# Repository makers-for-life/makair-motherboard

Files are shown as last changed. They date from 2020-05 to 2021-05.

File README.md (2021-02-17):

# MakAir Motherboard

## Versions

| Version | Last Changelog | Ready? | Schematics | Live CAD Models |
| ------- | -------------- | ------ | ---------- | --------------- |
| V1.1 | Working PCB w/ software | ✅ | none | none
| V2.0 | Version Two | ✅ | [view schematic](./src/schematics/Archives/V2/Electrical%20Schematics.pdf) | none
| V3.0 | Added pressure sensors + more systems have been integrated on the board | ✅ | [view schematic](./src/schematics/V3/Electrical%20Schematics.pdf) | [view model](https://a360.co/3eaMoN0)

## Notes

* All the electronics schematics and PCB designs were made by engineers from [Tronico](https://www.tronico-alcen.com/en), a France-based electronic systems designers and manufacturer, with on-site PCB manufacturing capabilities.

## Renders

### Final Motherboard

<p align="center">
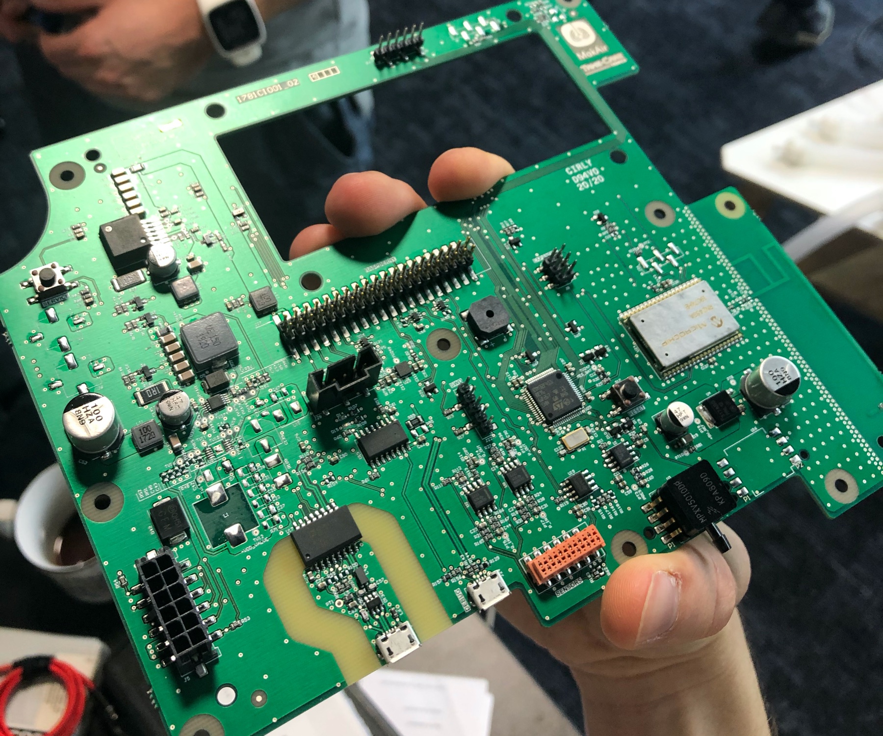
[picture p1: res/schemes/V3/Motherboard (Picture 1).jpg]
Motherboard Picture
  
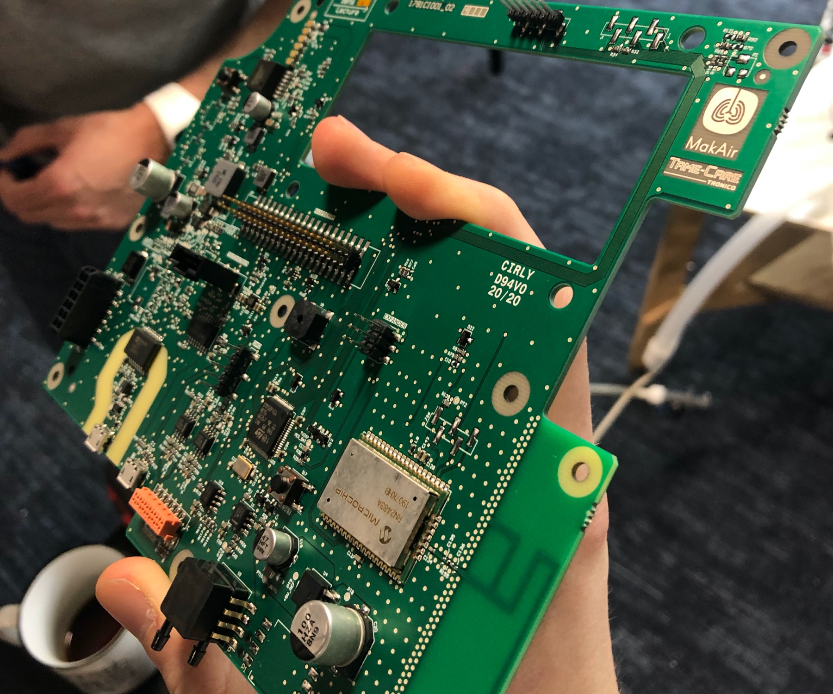
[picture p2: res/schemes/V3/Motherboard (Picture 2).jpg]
Motherboard Picture
  
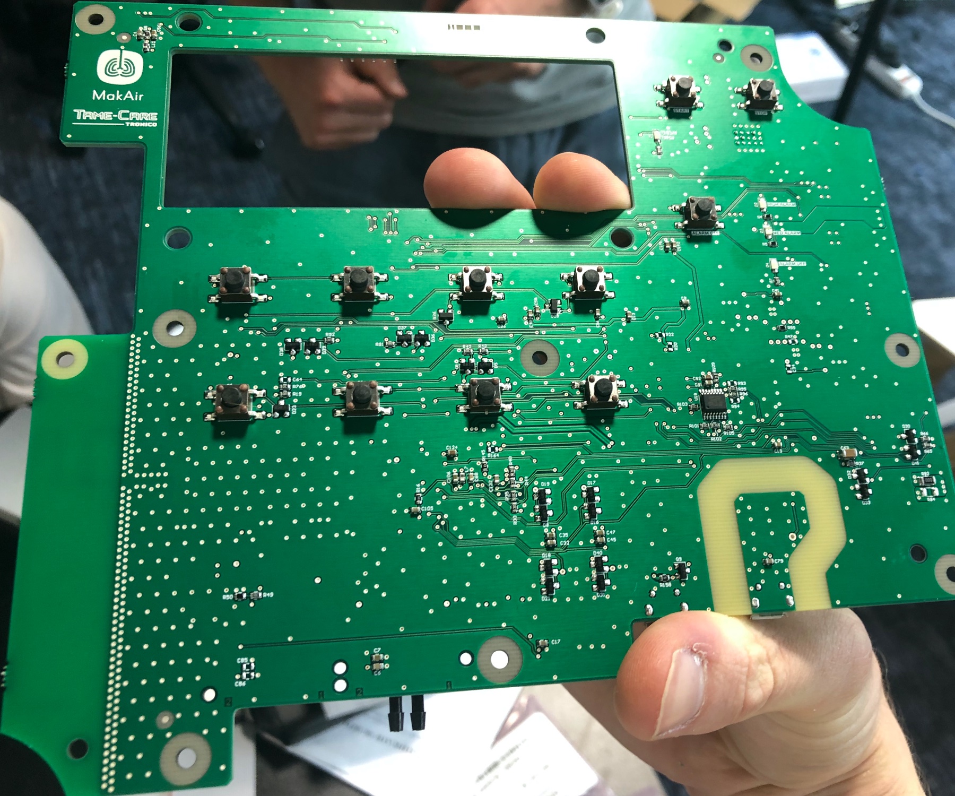
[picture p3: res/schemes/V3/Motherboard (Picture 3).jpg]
Motherboard Picture
  
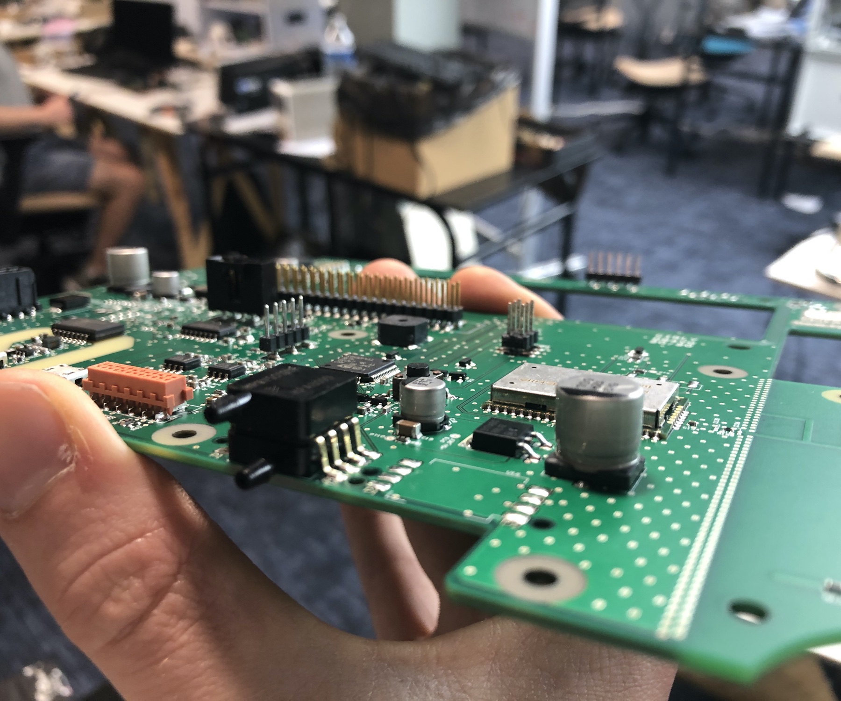
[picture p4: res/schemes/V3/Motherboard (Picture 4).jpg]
Motherboard Picture
  
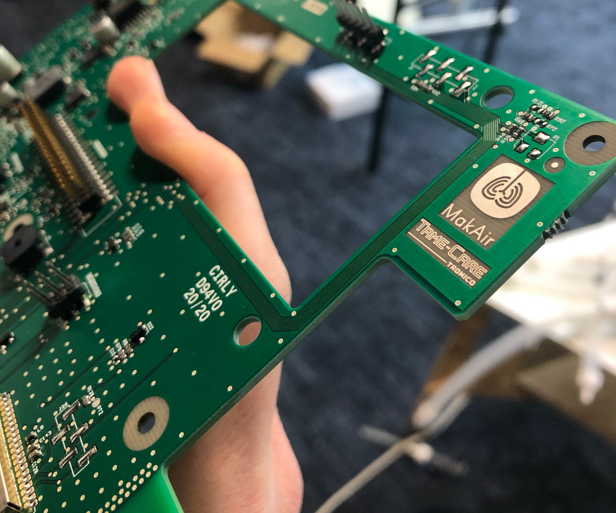
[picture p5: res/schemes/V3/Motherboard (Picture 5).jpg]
Motherboard Picture
  
</p>

### Gerbers

<p align="center">
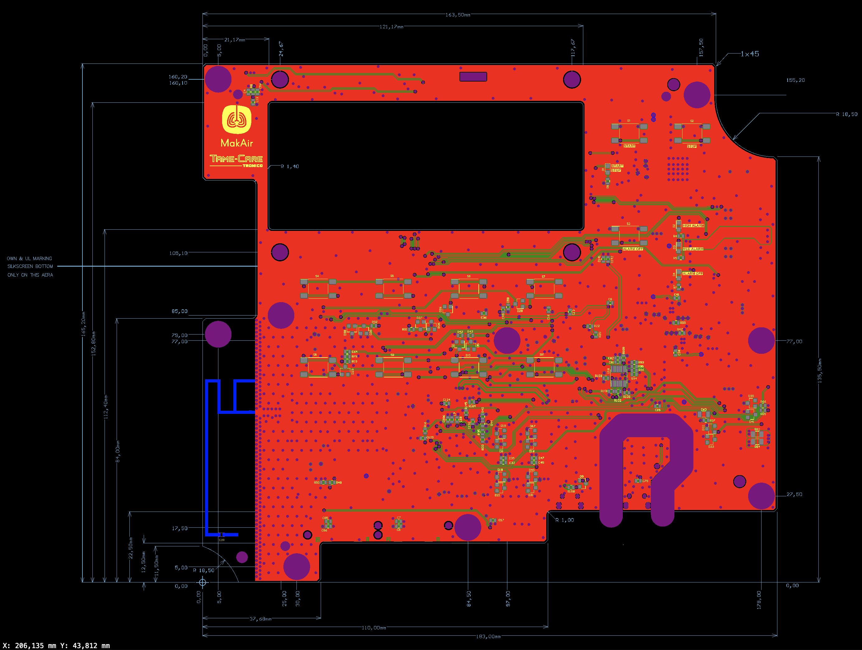
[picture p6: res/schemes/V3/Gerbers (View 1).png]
Gerbers View
  
</p>

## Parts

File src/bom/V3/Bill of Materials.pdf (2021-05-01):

Designation : RESP. ARTIFICIEL V3.1 | | Author by : vlecunff
Customer : TRONICO | Date : 28/05/2020 | Signature :
Reference : 1781LC001 | Revision : 02 | Verified by : pboiziau
Customer Reference : 099 | | Signature :
Level | Reference designator | ID_RnD | Item Code | Description | Quantity | Commentary
1 | 2 | 3 | 4 | | | | Short Description | Long Description | Manufacturer & Part Number
* | | | | C1-C6,C8,C11-C17,C23,C24,C30-C32,C36,C41,C44,C45,C49,C 58,C60-C62,C66,C69,C71,C72,C74,C 76-C81,C88-C90,C92-C97,C105,C107,C127,C128,C 131,C132,C142 | 23U00036 | 00280K676A | COND_CERAM CMS 0603 X7R | 100nF 50V 10% -55°C/+125°C | AVX 06035C104KAT2A | 55
* | | | | C7,C35,C47,C56,C59,C70,C8 3,C91,C106,C111-C113,C141,C143 | 23U00347 | 00280K522A | COND_CERAM CMS 0603 X5R | 1uF 50V 10% -55°C/+85°C | TDK CGA3E3X5R1H105K080AB | 14
* | | | | C9 | 23U00388 | 00280K526A | COND_CERAM CMS 0603 C0G | 470pF 50V 5% -55°C/+125°C | KEMET C0603C471J5GACTU | 1
* | | | | C10,C34,C64,C65,C73,C85,C 130 | | | | | | NC
* | | | | C18,C98,C140 | 21U00041 | 002504131A | COND_ALUM CMS D:6.3mm | 47uF 50V 20% 680mR -55°C/+105°C | PANASONIC EEEFT1H470AP | 3
* | | | | C19,C25,C26,C37-C40,C63,C99 | 23U00488 | 00280K521A | COND_CERAM CMS 1206 X5R | 10uF 50V 10% -55°C/+85°C | MURATA GRM31CR61H106KA12L | 9
* | | | | C20,C53 | 21U00015 | 002504142A | COND_ALUM CMS D:10mm | 100uF +50V 20% 28mR -55°C/+105°C | PANASONIC EEHZA1H101P | 2
* | | | | C21,C22,C27-C29,C33,C67 | | | | | | NC
* | | | | C42 | | | | | | NC
* | | | | C43 | | | | | | NC
* | | | | C46 | | | | | | NC
* | | | | C48,C54 | | | | | | NC
* | | | | C50 | 23U00055 | 00280K524A | COND_CERAM CMS 0603 C0G | 6.8pF 50V 0.25pF -55°C/+125°C | KEMET C0603C689C5GACTU | 1
* | | | | C51 | 23U00490 | 00280K523A | COND_CERAM CMS 0603 X7R | 4.7nF 50V 5% -55°C/+125°C | KEMET C0603C472J5RACTU | 1
* | | | | C52,C68 | 23U00104 | 00280K634A | COND_CERAM CMS 0603 X7R | 10nF 50V 10% -55°C/+125°C | KEMET C0603C103K5RACTU | 2
* | | | | C55,C57,C122,C123 | 23U00046 | 00280K636A | COND_CERAM CMS 0603 C0G | 22pF 50V 10% -55°C/+125°C | KEMET C0603C220K5GACTU | 4
* | | | | C82,C124 | 23U00282 | 00280K682A | COND_CERAM CMS 0603 X5R | 4.7uF 25V 10% -55°C/+85°C | MURATA GRM188R61E475KE15D | 2
* | | | | C86 | | | | | | NC
* | | | | C100-C104,C114 | 23U00492 | 00280K635A | COND_CERAM CMS 1206 X5R | 22µF 25V 20% -55°C/+85°C | MURATA GRT31CR61E226ME01L | 6
* | | | | C109,C110 | 23U00059 | 00280K681A | COND_CERAM CMS 0603 X7R | 22nF 16V 10% -55°C/+125°C | KEMET C0603C223K4RACTU | 2
* | | | | C134 | 23U00494 | 00280K642A | COND_CERAM CMS 0402 COG HF | 56pF 100V 1% -55°C/+125°C | KEMET CBR04C560F1GAC | 1
* | | | | C135,C136 | | | | | | NC
* | | | | C139 | | | | | | NC
Soudure : | SAC

26 RUE DU BOCAGE CS 20660
ST PHILBERT DE BOUAINE
85607 MONTAIGU CEDEX
Tél : +33 (0)2 51 41 91 35 Fax : +33 (0)2 51 41 94 27
ET68/D | STRICTEMENT CONFIDENTIEL TRONICO | 1/5

Reference : 1781LC001 | Revision : 02 | Verified by : pboiziau
Customer Reference : 099 | | Signature :
Level | Reference designator | ID_RnD | Item Code | Description | Quantity | Commentary
1 | 2 | 3 | 4 | | | | Short Description | Long Description | Manufacturer & Part Number
* | | | | CI1 | I1U00004 | 00590G851A | CIRCUIT IMPRIME RESP. ARTIFICIEL V3.1 | 1781CI001 | SPECIF 1781PCB0001_05 PLAN 1781CI001 IND05 GERBERS 1781GER001 IND05 PANNEAU PAN099MAKR694 IND00 | 1
* | | | | D1,D4 | E1U00030 | 004109304A | DIODE_LED VERTE CMS 0805 | 520 78mW 3.4V 20mA -40°C/+85°C -40°C/+85°C | AVAGO HSMQ-C170 | 2
* | | | | D2 | E1U00031 | 004109305A | DIODE_LED ROUGE CMS 0805 | 637 60mW 2.4V 25mA -40°C/+85°C -40°C/+85°C | AVAGO HSMC-C170 | 1
* | | | | D3 | E1U00032 | 004109306A | DIODE_LED JAUNE CMS 0805 | 591 85mcd 2.05V 20mA -40°C/+85°C -40°C/+90°C | Everlight Electronics EAST2012YA2 | 1
* | | | | D5,D6,D8,D10-D12,D16-D19,D21,D30-D33,D36-D41 | 33U00013 | 00415E364A | DIODE_DE_SIGNAL CMS SOT23 | 30V 200mA -55°C/+150°C -55°C/+150°C | FAIRCHILD BAT54 | 21
* | | | | D7 | | | | | | NC
* | | | | D9 | 39U00073 | 004109287A-RD | DIODE_SCHOTTKY CMS SMB | 40V 3A SINGLE -40°C/+105°C -65°C/+150°C | ST MICROELECTRONICS STPS340U | 1
* | | | | D13 | 38U00032 | 00415E388A | DIODE_ESD CMS SOT23-6L UNI | 15kV DUAL -40°C/+125°C -55°C/+150°C | ST MICROELECTRONICS USBLC6-2SC6 | 1
* | | | | D14,D15,D20 | E1U00022 | 00415E387A | DIODE_LED VERTE CMS 0402 | 574nm 3.5mcd 1.9V 2mA -40°C/+85°C -40°C/+85°C | KINGBRIGHT APHHS1005LCGCK | 3
* | | | | D22-D29 | 33U00002 | 00415E389A | DIODE_DE_SIGNAL CMS SOT23 | 85V 200mA -55°C/+150°C -55°C/+150°C | FAIRCHILD BAS16 | 8
* | | | | D34 | 38U00011 | 00415E415A | DIODE_ESD CMS SOT553 UNI | 8kV 0.9V-5.5V DUAL -40°C/+85°C -65°C/+150°C | TEXAS INSTRUMENTS TPD2E001DRLR | 1
* | | | | D42 | 36U00007 | 00415E363A | DIODE_TRANSIL CMS DO-214AB BI | 33V 1500W -55°C/+150°C -55°C/+150°C | FAIRCHILD SMCJ33CA | 1
* | | | | ET1 | G1U00004 | - | ETIQUETTE IDENTIFICATION | 1781ET001 | PLAN 1781ET001 IND01 | 1
| * | | | - | - | CONSOM1071 | ETIQU ETIQU POLYIMIDE AMBRE MAT | | BRADY THT-46-724-10 | 1
* | | | | F1 | 86U00021 | 00555A448A | FUSIBLE REARMABLE CMS 0603 | 500mA 6V THERM -40°C/+85°C | BOURNS MF-FSMF050X | 1
* | | | | J1,J3 | ABU00030 | 005169144A | BARRETTE MALE CMS 6PTS | DROIT SN P:2.54mm -55°C/+105°C | SAMTEC TSM-106-01-T-SV-P-TR | 2
* | | | | J2,J24 | A7U00249 | 005169160A | CONNECT USB CMS 5PTS | EMBASE RECT FEM COUDE -30°C/+85°C | HIROSE ZX62D-B-5PA8(30) | 2
* | | | | J4 | A7U00321 | 005169147A | CONNECT Micro Match CMS 12PTS | EMBASE RECT FEM DROIT | TE CONNECTIVITY 1-188275-2 | 1
* | | | | J5 | A7U00305 | 005169145A | CONNECT MICRO-FIT CMS 2x6PTS | EMBASE RECT MALE DROIT -40°C/+105°C -40°C/+105°C | MOLEX 43045-1218 | 1
Soudure : | SAC

26 RUE DU BOCAGE CS 20660
ST PHILBERT DE BOUAINE
85607 MONTAIGU CEDEX
Tél : +33 (0)2 51 41 91 35 Fax : +33 (0)2 51 41 94 27

Reference : 1781LC001 | Revision : 02 | Verified by : pboiziau
Customer Reference : 099 | | Signature :
Level | Reference designator | ID_RnD | Item Code | Description | Quantity | Commentary
1 | 2 | 3 | 4 | | | | Short Description | Long Description | Manufacturer & Part Number
* | | | | J6,J7 | | | | | | NC
* | | | | J8 | A7U00323 | 005169124A | CONNECT C-Grid CMS 2x3PTS | EMBASE RECT MALE DROIT -40°C/+105°C | MOLEX 0015912060 | 1
* | | | | J9 | A7U00339 | 005169170A | CONNECT PCB HEADER CMS 4PTS | EMBASE RECT MALE DROIT -25°C/+85°C | JST B4B-PH-SM4-TB(LF)(SN) | 1
* | | | | J10 | | | | | | NC
* | | | | J22 | A7U00320 | 005169159A | BARRETTE MALE CMS 5PTS | DROIT SN P:2.54mm -55°C/+105°C | SAMTEC TSM-105-01-T-SV | 1
* | | | | J26 | | | | | | NC
* | | | | J27 | A7U00330 | 005169149A | CONNECT CMS 2x20PTS | EMBASE RECT MALE DROIT -40°C/+105°C | CNC TECH 3020-40-0300-00 | 1
* | | | | J28 | A7U00327 | 005169148A | CONNECT SL CMS 5PTS | EMBASE RECT MALE DROIT -40°C/+105°C | MOLEX 74099-1005 | 1
* | | | | L1 | | | | | | NC
* | | | | L3 | 42U00158 | 003115800A | SELF CMS 1040 | 15uH 20% 8.5A -40°C/+125°C | WURTH ELEKTRONIK 74437368150 | 1
* | | | | L4 | 48U00023 | 003115846A | SELF_MODE_COMMUN CMS 1206TS | 90R 25% 370mA 50V -40°C/+125°C | PULSE ELECTRONICS PE-1206CCMC900STS | 1
* | | | | L5,L6 | 43U00020 | 003115845A | FERRITES CMS 0603 | 600R 100MHz 200mA -55°C/+125°C -20°C/+60°C | WURTH ELEKTRONIK 74279265 | 2
* | | | | L7 | 42U00090 | 003115847A | SELF CMS 0603 | 120nH 5% 300mA -40°C/+85°C | KEMET L0603CR12JRMST | 1
* | | | | L8,L12 | 43U00016 | 003115836A | FERRITES CMS 0603 | 220R 100MHz 2.5A -55°C/+125°C -55°C/+125°C | MURATA BLM18SG221TN1D | 2
* | | | | L10 | | | | | | NC
* | | | | L11,L13,L16 | 42U00140 | 003115837A | SELF CMS 5.2x5.7x1.8mm | 10µH 20% 3.4A -40°C/+150°C -40°C/+150°C | BOURNS SRP5020TA-100M | 3
* | | | | P1 | | | | | | NC
* | | | | Q1,Q2,Q4-Q8 | 92U00012 | 004234241A | TRANSISTOR_MOS CMS SOT23 | CANAL N 60V 0.36A -55°C/+150°C -65°C/+150°C | NEXPERIA 2N7002P,215 | 7
* | | | | Q3 | 92U00048 | 004234251A | TRANSISTOR_MOS CMS SOT23-6L | CANAL P 30V 4A -55°C/+150°C | ST MICROELECTRONICS STT4P3LLH6 | 1
* | | | | Q9 | 91U00003 | 004234238A | TRANSISTOR_BIP CMS SOT23 | NPN 30V +0.6A -55°C/+150°C -55°C/+150°C | ON SEMICONDUCTOR MMBT2222LT1G | 1
* | | | | R1,R7,R9,R10,R19,R32,R43,R 53,R54,R63,R72-R74,R83,R91,R92,R131,R136 ,R147-R150,R168,R170 | 11U00071 | 00140AA4045A | REST CMS 0603 100PPM | 100R 1/10W 1% -55°C/+155°C | YAGEO RC0603FR-07100RL | 24
* | | | | R2,R3,R6,R11,R27,R31,R33-R35,R41,R42,R57,R59-R61,R64,R75-R77,R87,R88,R95-R98,R101-R103,R105,R111,R116,R117, R119,R130,R135,R139,R151-R154,R156,R165 | 11U00108 | 00140AA4035A | REST CMS 0603 100PPM | 10kR 1/10W 1% -55°C/+155°C | YAGEO RC0603FR-0710KL | 42
Soudure : | SAC

26 RUE DU BOCAGE CS 20660
ST PHILBERT DE BOUAINE
85607 MONTAIGU CEDEX
Tél : +33 (0)2 51 41 91 35 Fax : +33 (0)2 51 41 94 27

Reference : 1781LC001 | Revision : 02 | Verified by : pboiziau
Customer Reference : 099 | | Signature :
Level | Reference designator | ID_RnD | Item Code | Description | Quantity | Commentary
1 | 2 | 3 | 4 | | | | Short Description | Long Description | Manufacturer & Part Number
* | | | | R4,R5 | 11U01011 | 00140AA4043A | REST CMS 0603 200PPM | 180R 1/10W 1% 75V -55°C/+155°C | VISHAY CRCW0603180RJNEA | 2
* | | | | R8,R26 | 11U00074 | 00140AA4042A | REST CMS 0603 100PPM | 150R 1/10W 1% -55°C/+155°C | YAGEO RC0603FR-07150RL | 2
* | | | | R12,R69,R79,R81,R90,R109, R123-R128,R143-R145,R163 | 11U00009 | 00140AA4037A | REST CMS 0603 100PPM | 0R 1/10W 20mR -55°C/+155°C | VISHAY CRCW06030000Z0EA | 16
* | | | | R13,R17,R106,R110 | 11U01018 | 00140AA4054A | REST CMS 0603 100PPM | 33R 1/10W 5% 75V -55°C/+155°C | YAGEO RC0603JR-0733RL | 4
* | | | | R14,R62,R70,R121,R122,R13 3,R169,R171 | | | | | | NC
* | | | | R15,R18,R21,R25,R112 | 11U00106 | 00140AA4032A | REST CMS 0603 100PPM | 220R 1/10W 1% -55°C/+155°C | YAGEO RC0603FR-07220RL | 5
* | | | | R16,R45,R158 | 11U01012 | 00140AA4047A | REST CMS 0603 100PPM | 1.6kR 1/10W 1% 75V -55°C/+155°C | VISHAY CRCW06031K60FKEA | 3
* | | | | R20,R22,R51,R93,R94,R99,R 100,R104,R115,R118,R132,R 164 | | | | | | NC
* | | | | R23,R24,R113,R166 | 11U00156 | 00140AA4039A | REST CMS 0603 100PPM | 470R 1/10W 1% -55°C/+155°C | YAGEO RC0603FR-07470RL | 4
* | | | | R28,R107,R108,R120 | 11U00072 | 00140AA4048A | REST CMS 0603 100PPM | 680R 1/10W 1% -55°C/+155°C | YAGEO RC0603FR-07680RL | 4
* | | | | R29 | 11U00585 | 00140AA4049A | REST CMS 0603 100PPM | 8.2kR 1/10W 1% -55°C/+155°C | YAGEO RC0603FR-078K2L | 1
* | | | | R30 | 11U00110 | 00140AA4038A | REST CMS 0603 100PPM | 1kR 1/10W 1% -55°C/+155°C | YAGEO RC0603FR-071KL | 1
* | | | | R36,R38,R114,R167 | 11U00282 | 00140AA4053A | REST CMS 0603 100PPM | 910R 1/10W 1% -55°C/+155°C | YAGEO RC0603FR-07910RL | 4
* | | | | R37 | 11U00977 | 00140AA4040A | REST CMS 0603 100PPM | 3kR 1/10W 1% -55°C/+155°C | YAGEO RC0603FR-073KL | 1
* | | | | R39,R161 | 11U01009 | 00140AA4034A | REST CMS 2512 100PPM | 1R 1.5W 1% 500V -55°C/+155°C | VISHAY CRCW25121R00FKEGHP | 2
* | | | | R40,R44,R134 | 11U00069 | 00140AA4125A | REST CMS 0603 100PPM | 4.7kR 1/10W 1% -55°C/+155°C | YAGEO RC0603FR-074K7L | 3
* | | | | R46 | 11U00079 | 00140AA4055A | REST CMS 0603 100PPM | 330R 1/10W 1% -55°C/+155°C | YAGEO RC0603FR-07330RL | 1
* | | | | R47 | | | | | | NC
* | | | | R48 | | | | | | NC
* | | | | R49 | 11U01020 | 00140AA3976A | REST CMS 0603 25PPM | 330R 1/10W 0.1% 75V -55°C/+85°C | PANASONIC ERA-3AEB331V | 1
* | | | | R50 | 11U00834 | 00140AA4154A | REST CMS 0603 10PPM | 1kR 1/8W 0.1% 75V -55°C/+155°C | VISHAY TNPW06031K00BYEN | 1
* | | | | R52 | | | | | | NC
* | | | | R55,R129 | 11U01019 | 00140AA4051A | REST CMS 0603 100PPM | 220kR 1/10W 1% 75V -55°C/+155°C | YAGEO RC0603FR-07220KL | 2
* | | | | R56,R157 | 11U01013 | 00140AA4046A | REST CMS 0603 100PPM | 44.2kR 1/10W 1% 75V -55°C/+155°C | VISHAY CRCW060344K2FKEA | 2
* | | | | R58 | 11U01017 | 00140AA4052A | REST CMS 0603 100PPM | 52.3kR 1/10W 1% 75V -55°C/+155°C | YAGEO RC0603FR-0752K3L | 1
* | | | | R65 | 11U01021 | 00140AA3973A | REST CMS 0603 100PPM | 200kR 1/10W 1% 75V -55°C/+155°C | YAGEO RC0603FR-07200KL | 1
* | | | | R66 | 11U00176 | 00140AA4060A | REST CMS 0603 100PPM | 27kR 1/10W 1% -55°C/+155°C | YAGEO RC0603FR-0727KL | 1
* | | | | R67 | 11U00111 | 00140AA3974A | REST CMS 0603 100PPM | 100kR 1/10W 1% -55°C/+155°C | YAGEO RC0603FR-07100KL | 1
* | | | | R68 | 11U01027 | 00140AA4124A | REST 0603 100PPM | 54.9kR 1/10W 1% 75V -55°C/+155°C | YAGEO RC0603FR-0754K9L | 1
* | | | | R71,R82,R85 | | | | | | NC
* | | | | R78,R80,R84,R89 | 11U00878 | 00140AA4050A | REST CMS 1206 | 0R 1/4W 20mR 3.5A -55°C/+155°C | VISHAY RCA12060000ZSEA | 4
* | | | | R86 | 11U01010 | 00140AA4041A | REST CMS 0603 100PPM | 62kR 1/10W 1% 75V -55°C/+155°C | VISHAY CRCW060362K0FKEA | 1
* | | | | R155 | 11U00352 | 00140AA3975A | REST CMS 0402 | 0R 20mR 1.5A -55°C/+155°C | VISHAY CRCW04020000Z0ED | 1
* | | | | R160 | | | | | | NC
* | | | | S1-S12,S17 | 81U00012 | 00580L320A | BOUTON_POUSSOIR CMS 4PTS | DROIT 12Vc.a. 50mA -35°C/+85°C | TE CONNECTIVITY 4-1437565-1 | 13
* | | | | SW1 | 82U00010 | 00580L449A | INTERRUPTEUR GLISSIERE CMS | DPDT DROIT +6Vdc;0.3A -40°C/+85°C -40°C/+85°C | C&K JS202011JCQN | 1
Soudure : | SAC

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

Reference : 1781LC001 | Revision : 02 | Verified by : pboiziau
Customer Reference : 099 | | Signature :
Level | Reference designator | ID_RnD | Item Code | Description | Quantity | Commentary
1 | 2 | 3 | 4 | | | | Short Description | Long Description | Manufacturer & Part Number
* | | | | U1,U2,U6 | 61U00068 | 00480P210A | CI_AOP_COMPAR CMS SO8 | DUAL AOP +2.2V/+5.5V L NOISE -40°C/+150°C -65°C/+150°C | TEXAS INSTRUMENTS OPA2365AIDG4 | 3
* | | | | U3 | 68U00002 | 00555A441A | CI_CAPTEUR_PRESSION CMS 1351 | ANALOG +4.75V/+5.25V 0PSI/1.45PSI 5% -40°C/+125°C -40°C/+125°C | NXP MPXV5010DP | 1
* | | | | U4 | 62U00134 | 00480P166A | CI_REGUL CMS DPAK | LIN +3V/+40V +1.2V/+37V LDO -40°C/+125°C -65°C/+150°C | ON SEMICONDUCTOR LM317MABDTRKG | 1
* | | | | U5 | | | | | | NC
* | | | | U7 | 62U00131 | 00480P000A | CI_REGUL CMS VSSOP10 | DEC +3.5V/+60V; +8V/+65V -40°C/+125°C | TEXAS INSTRUMENTS TPS54260DGQ | 1
* | | | | U8 | 74U00004 | 004412472A | BUZZER CMS 8.5x8.5x4 | TRANSD 4kHz +1V/+6V 100dBA -20°C/+70°C -40°C/+85°C | CUI INC CMT-8540S-SMT-TR | 1
* | | | | U9,U25,U26 | 67U00126 | 00480P167A | CI_DRIVER CMS SC70 | BUFFER -0.5V/+4.2V -40°C/+125°C -65°C/+150°C | TEXAS INSTRUMENTS 2N7001TDCKR | 3
* | | | | U13 | 51U00068 | 003500326A | ALIM DC/DC CMS 18W | +6V/+42V +0.8V/+6V +3A 90% -40°C/+125°C -65°C/+150°C | TEXAS INSTRUMENTS LMZ14203TZ-ADJ/NOPB | 1
* | | | | U15 | 64U00036 | 00480P020A | CI_MEMOIRE CMS SO16 | Voltage level Shifter +3V/+18V -55°C/+125°C -65°C/+150°C | TEXAS INSTRUMENTS CD40109BNSR | 1
* | | | | U16 | | | | | | NC
* | | | | U17 | 67U00125 | 00480P209A | CI_DRIVER CMS SO16W | USB +3.1V/+5.5V Isolation 5kV 12Mbps -40°C/+105°C -65°C/+150°C | ANALOG DEVICES ADUM4160BRIZ | 1
* | | | | U18 | 67U00086 | 00480P211A | CI_DRIVER CMS SSOP16 | UART/USB +2.97V/+5.5V -40°C/+85°C -65°C/+150°C | FTDI FT230XS | 1
* | | | | U19 | 64U00034 | 00480P212A | CI_MEMOIRE CMS SO8 | EEPROM +1.7V/+5.5V 2kB I2C -40°C/+85°C -65°C/+150°C | ST MICROELECTRONICS M24C02-FMN6TP | 1
* | | | | U20 | 65U00043 | 00480P113A-RD | CI_PROC CMS LQFP64 | uC +1.7V/+2.1V 8Bits 256kB -40°C/+85°C -60°C/+150°C | ST MICROELECTRONICS STM32F411RET6 | 1
* | | | | U23 | 62U00132 | 00480P165A | CI_REGUL CMS DFN6 | LIN +1.25V/+6V +3.3V/2A LDO -40°C/+125°C -55°C/+150°C | ST MICROELECTRONICS LD39200PU33R | 1
* | | | | U24 | 6FU00005 | 00480P164A | CI_MODULE CMS RN2483 LoRa | UART +2.1V/+3.6V Tx:14dBm/Rx:-148dBm 0 -40°C/+85°C -40°C/+115°C | MICROCHIP RN2483 | 1
* | | | | X1 | 73U00029 | 004412484A | QUARTZ CMS 6.0x3.6MM | 8MHZ 20PPM 18pF -20°C/+70°C -40°C/+85°C | ABRACON ABMM2-8.000MHZ-E2-T | 1
Soudure : | SAC

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

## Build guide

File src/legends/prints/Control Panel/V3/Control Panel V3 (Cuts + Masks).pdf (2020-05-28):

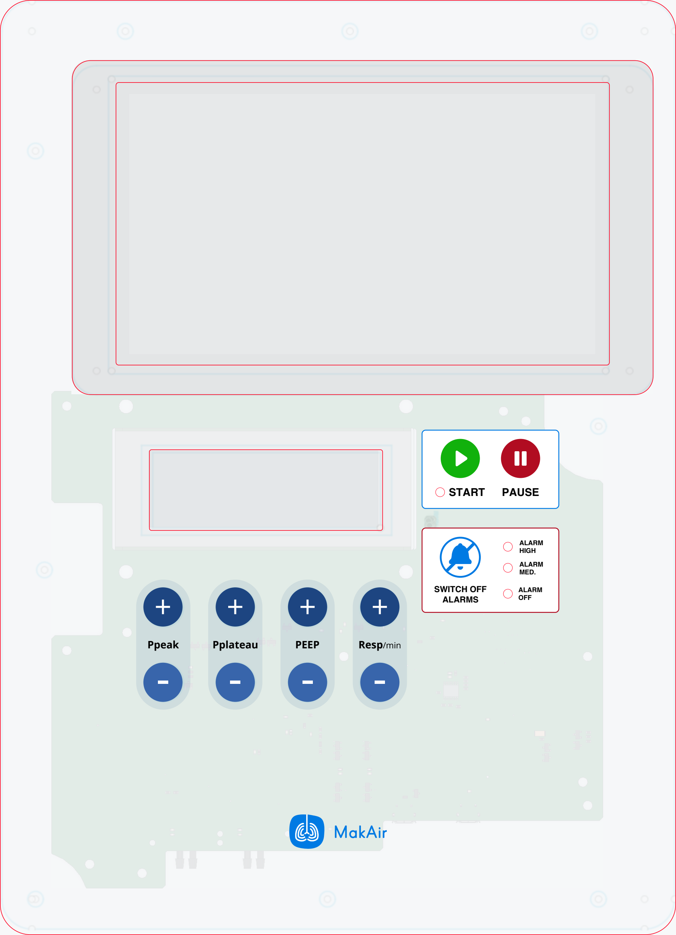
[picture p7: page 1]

START PAUSE

SWITCH OFF
ALARMS

ALARM
OFF

ALARM
MED.

ALARM
HIGH
Ppeak | Pplateau | PEEP | Resp/min
+ | + | + | +

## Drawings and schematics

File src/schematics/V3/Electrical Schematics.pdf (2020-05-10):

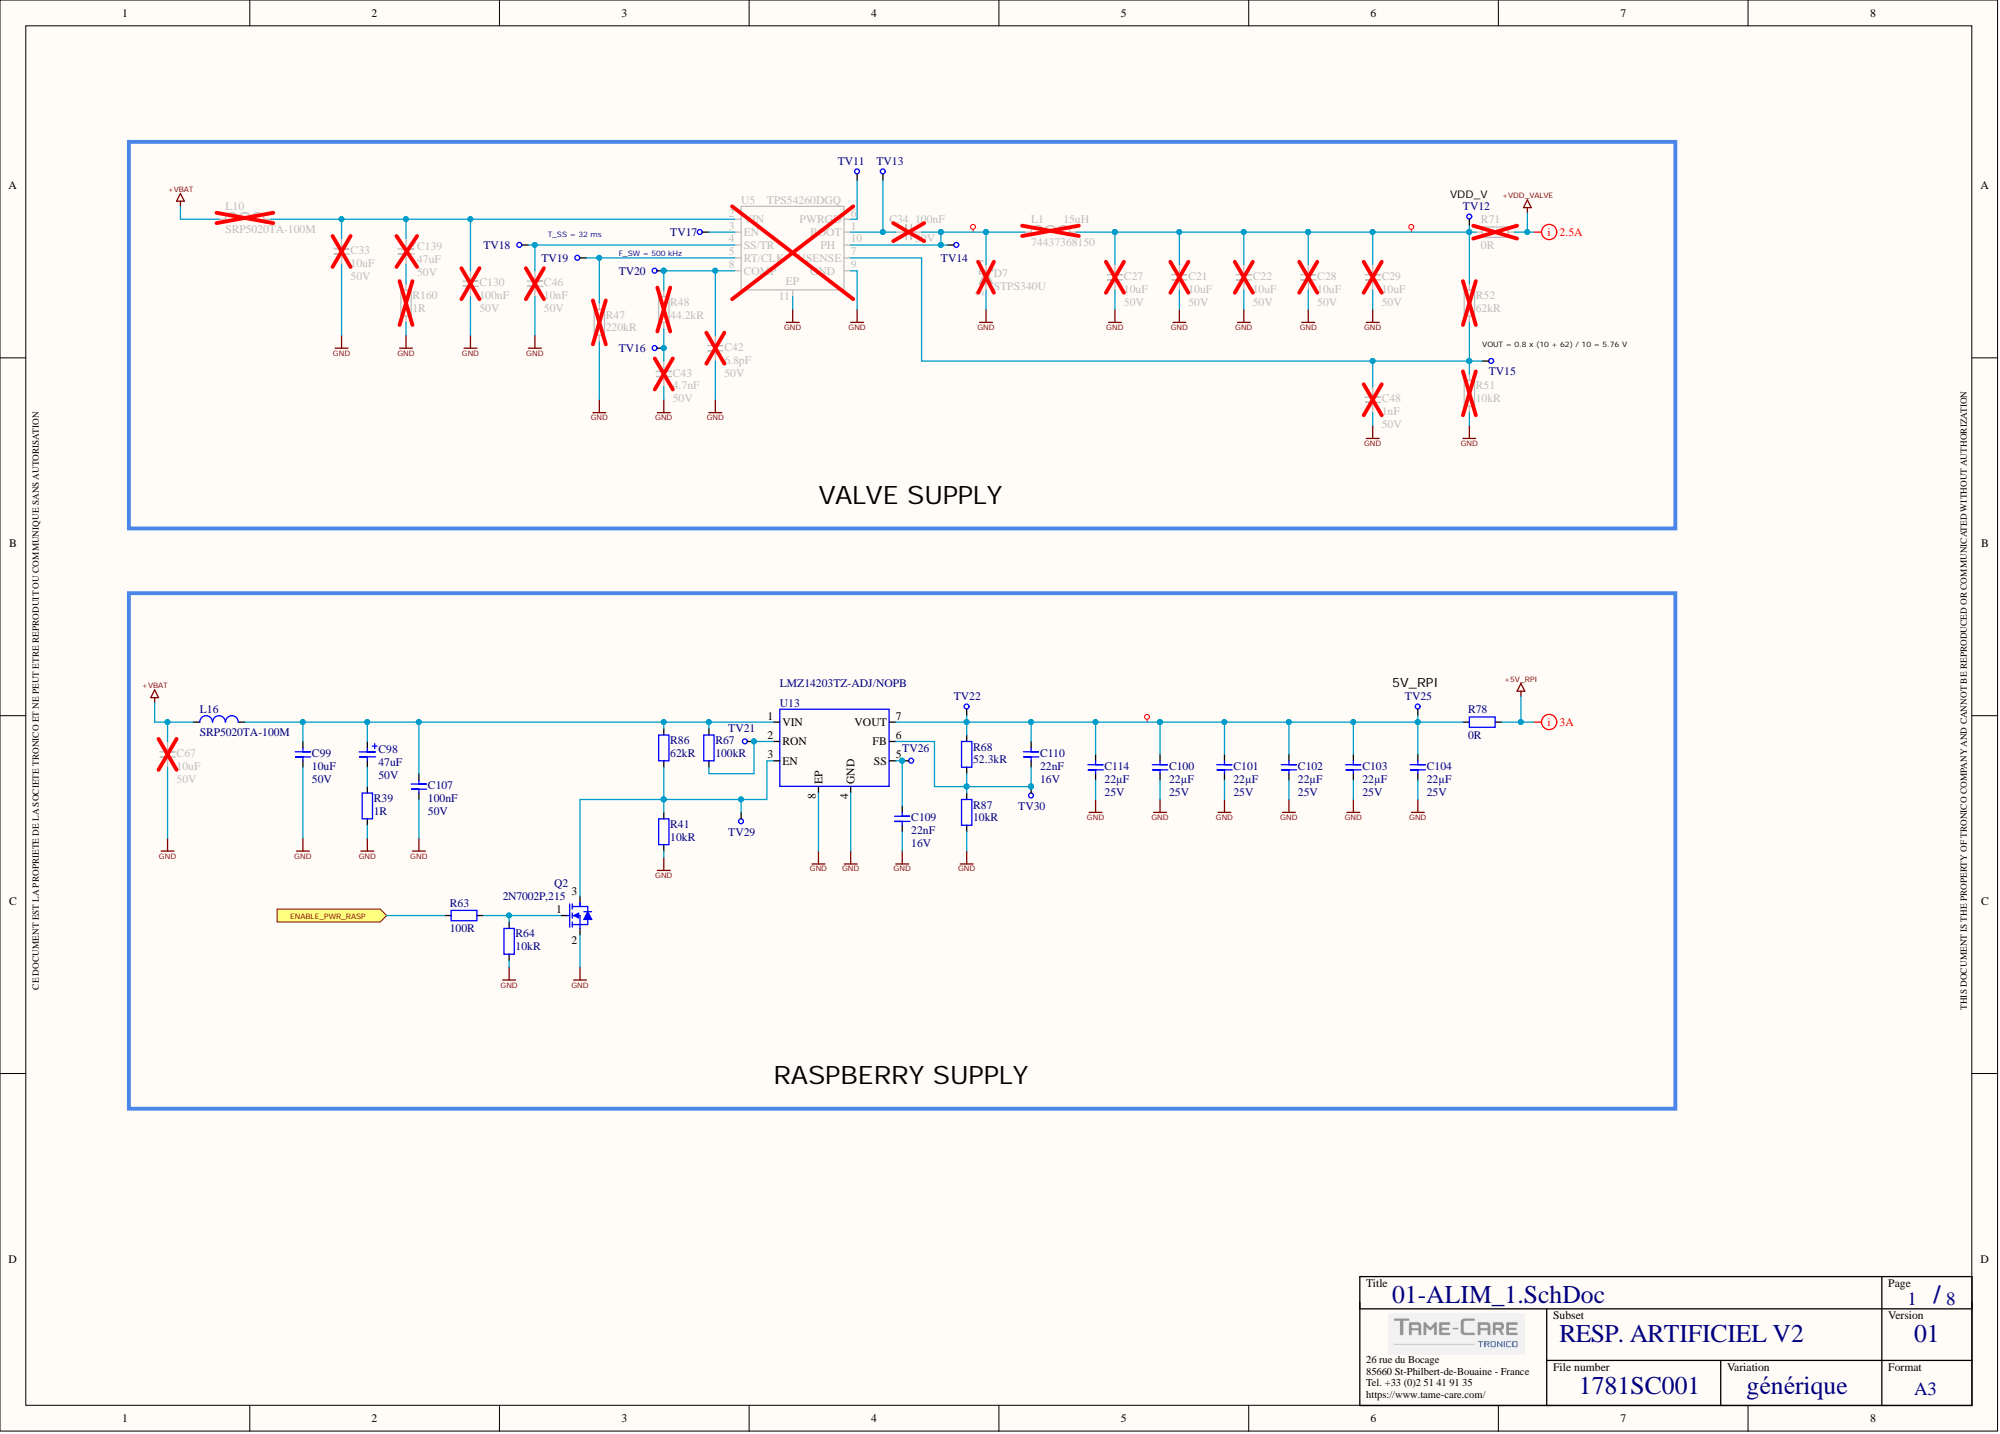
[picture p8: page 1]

THIS DOCUMENT IS THE PROPERTY OF TRONICO COMPANY AND CANNOT BE REPRODUCED OR COMMUNICATED WITHOUT AUTHORIZATION

CE DOCUMENT EST LA PROPRIETE DE LA SOCIETE TRONICO ET NE PEUT ETRE REPRODUIT OU COMMUNIQUE SANS AUTORISATION

Title 01-ALIM_1.SchDoc | Page 1 / 8

26 rue du Bocage 85660 St-Philbert-de-Bouaine - France Tel. +33 (0)2 51 41 91 35 https://www.tame-care.com/ | Subset RESP. ARTIFICIEL V2 | Version 01

File number 1781 SC001 | Variation générique | Format A3

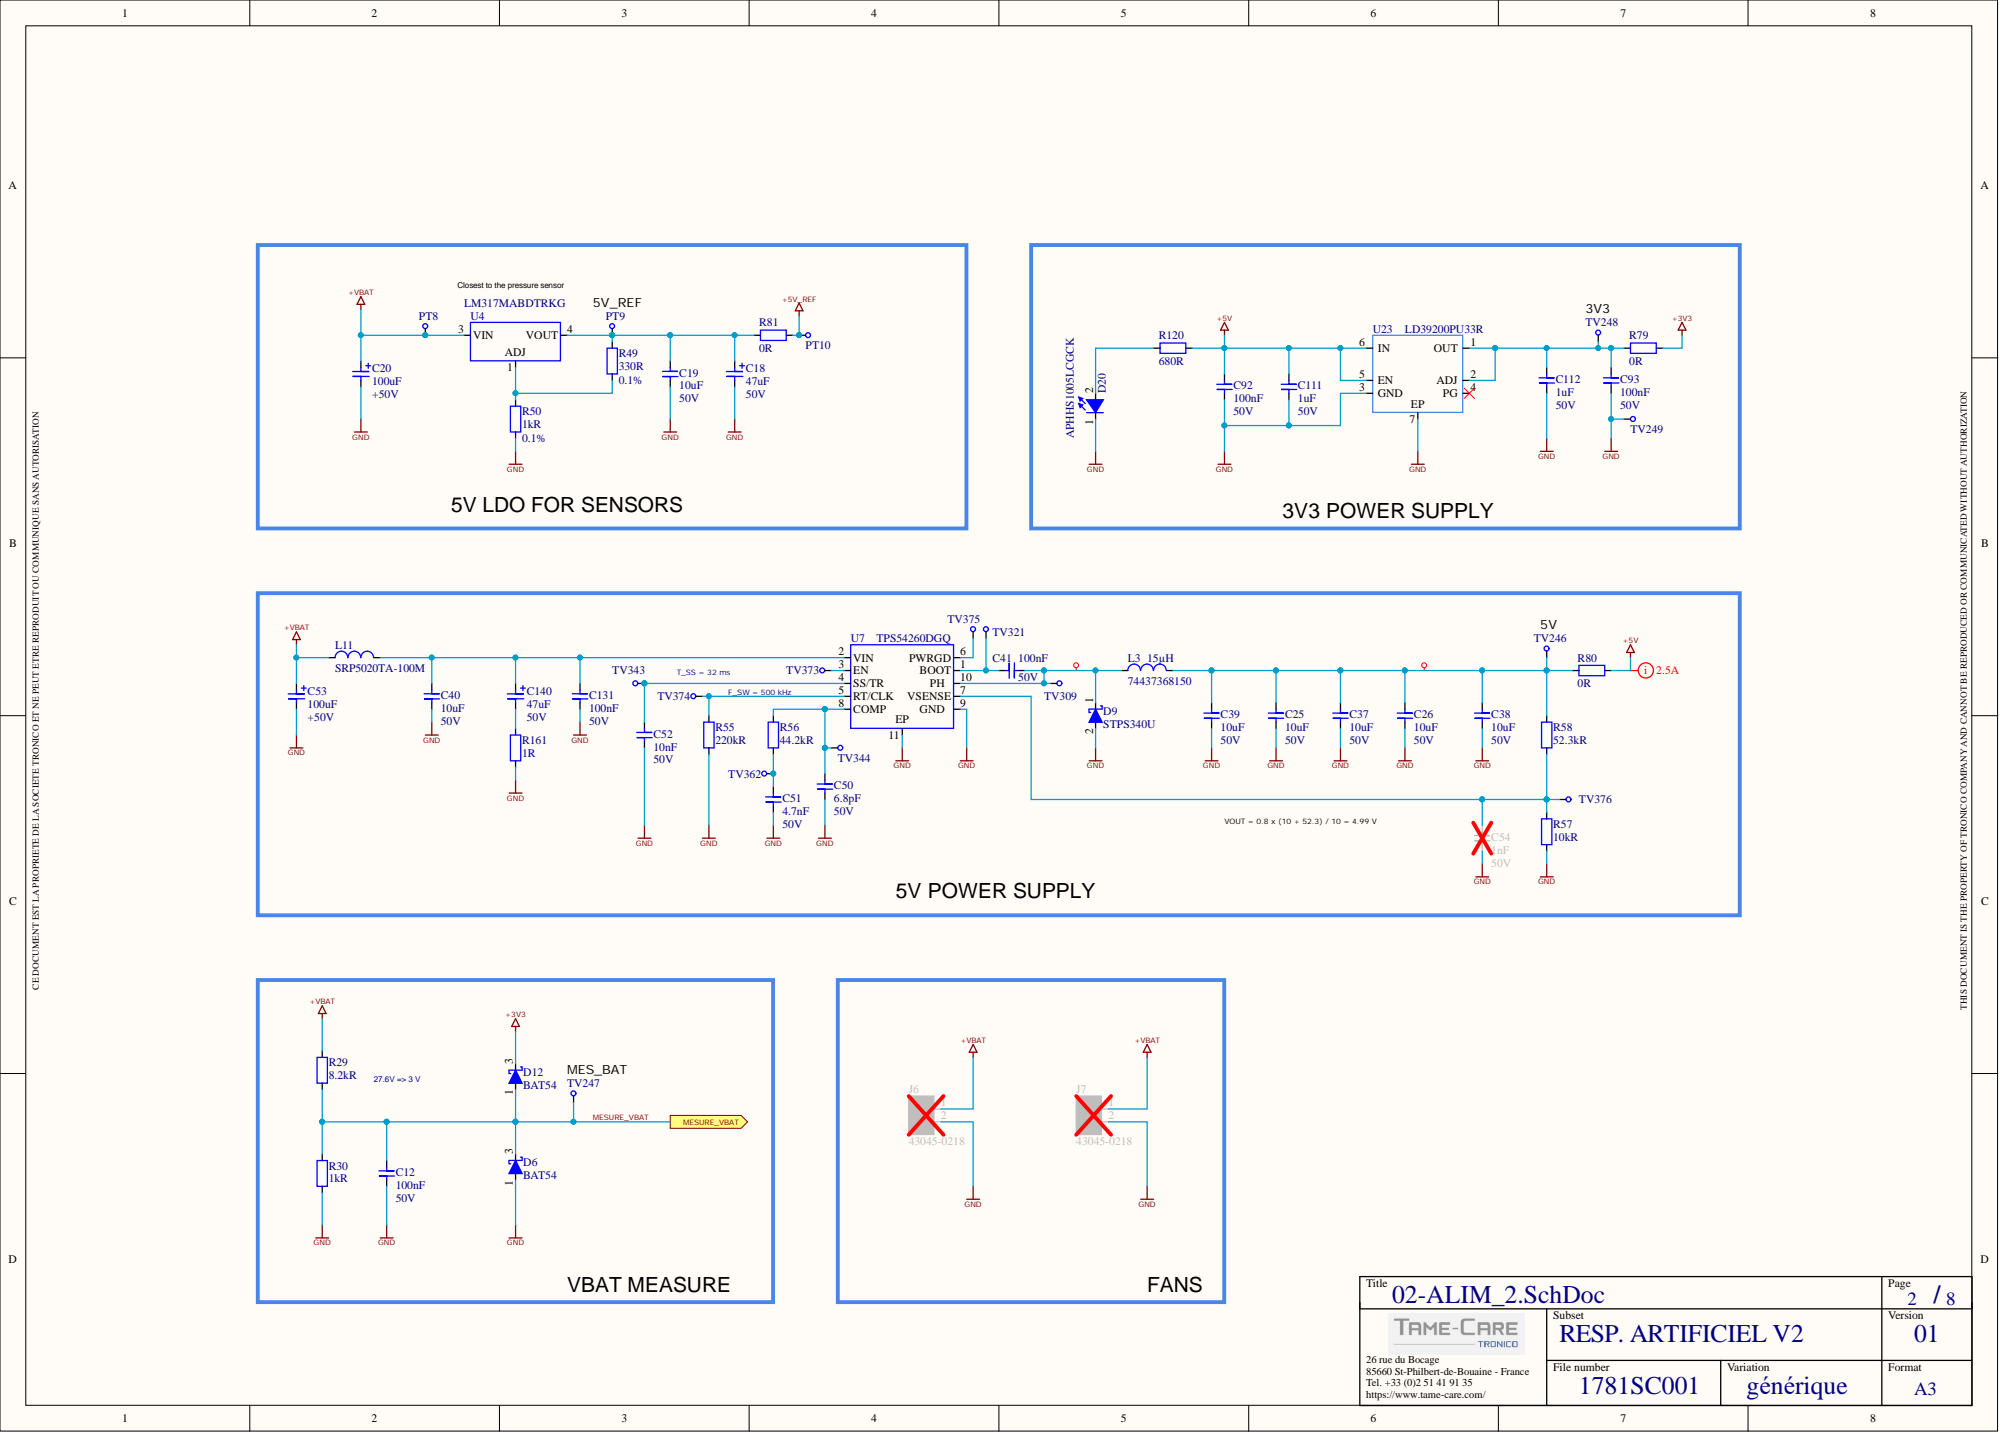
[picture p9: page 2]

THIS DOCUMENT IS THE PROPERTY OF TRONICO COMPANY AND CANNOT BE REPRODUCED OR COMMUNICATED WITHOUT AUTHORIZATION

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

GND | VBAT MEASURE

Title 02-ALIM_2.SchDoc | Page 2 / 8

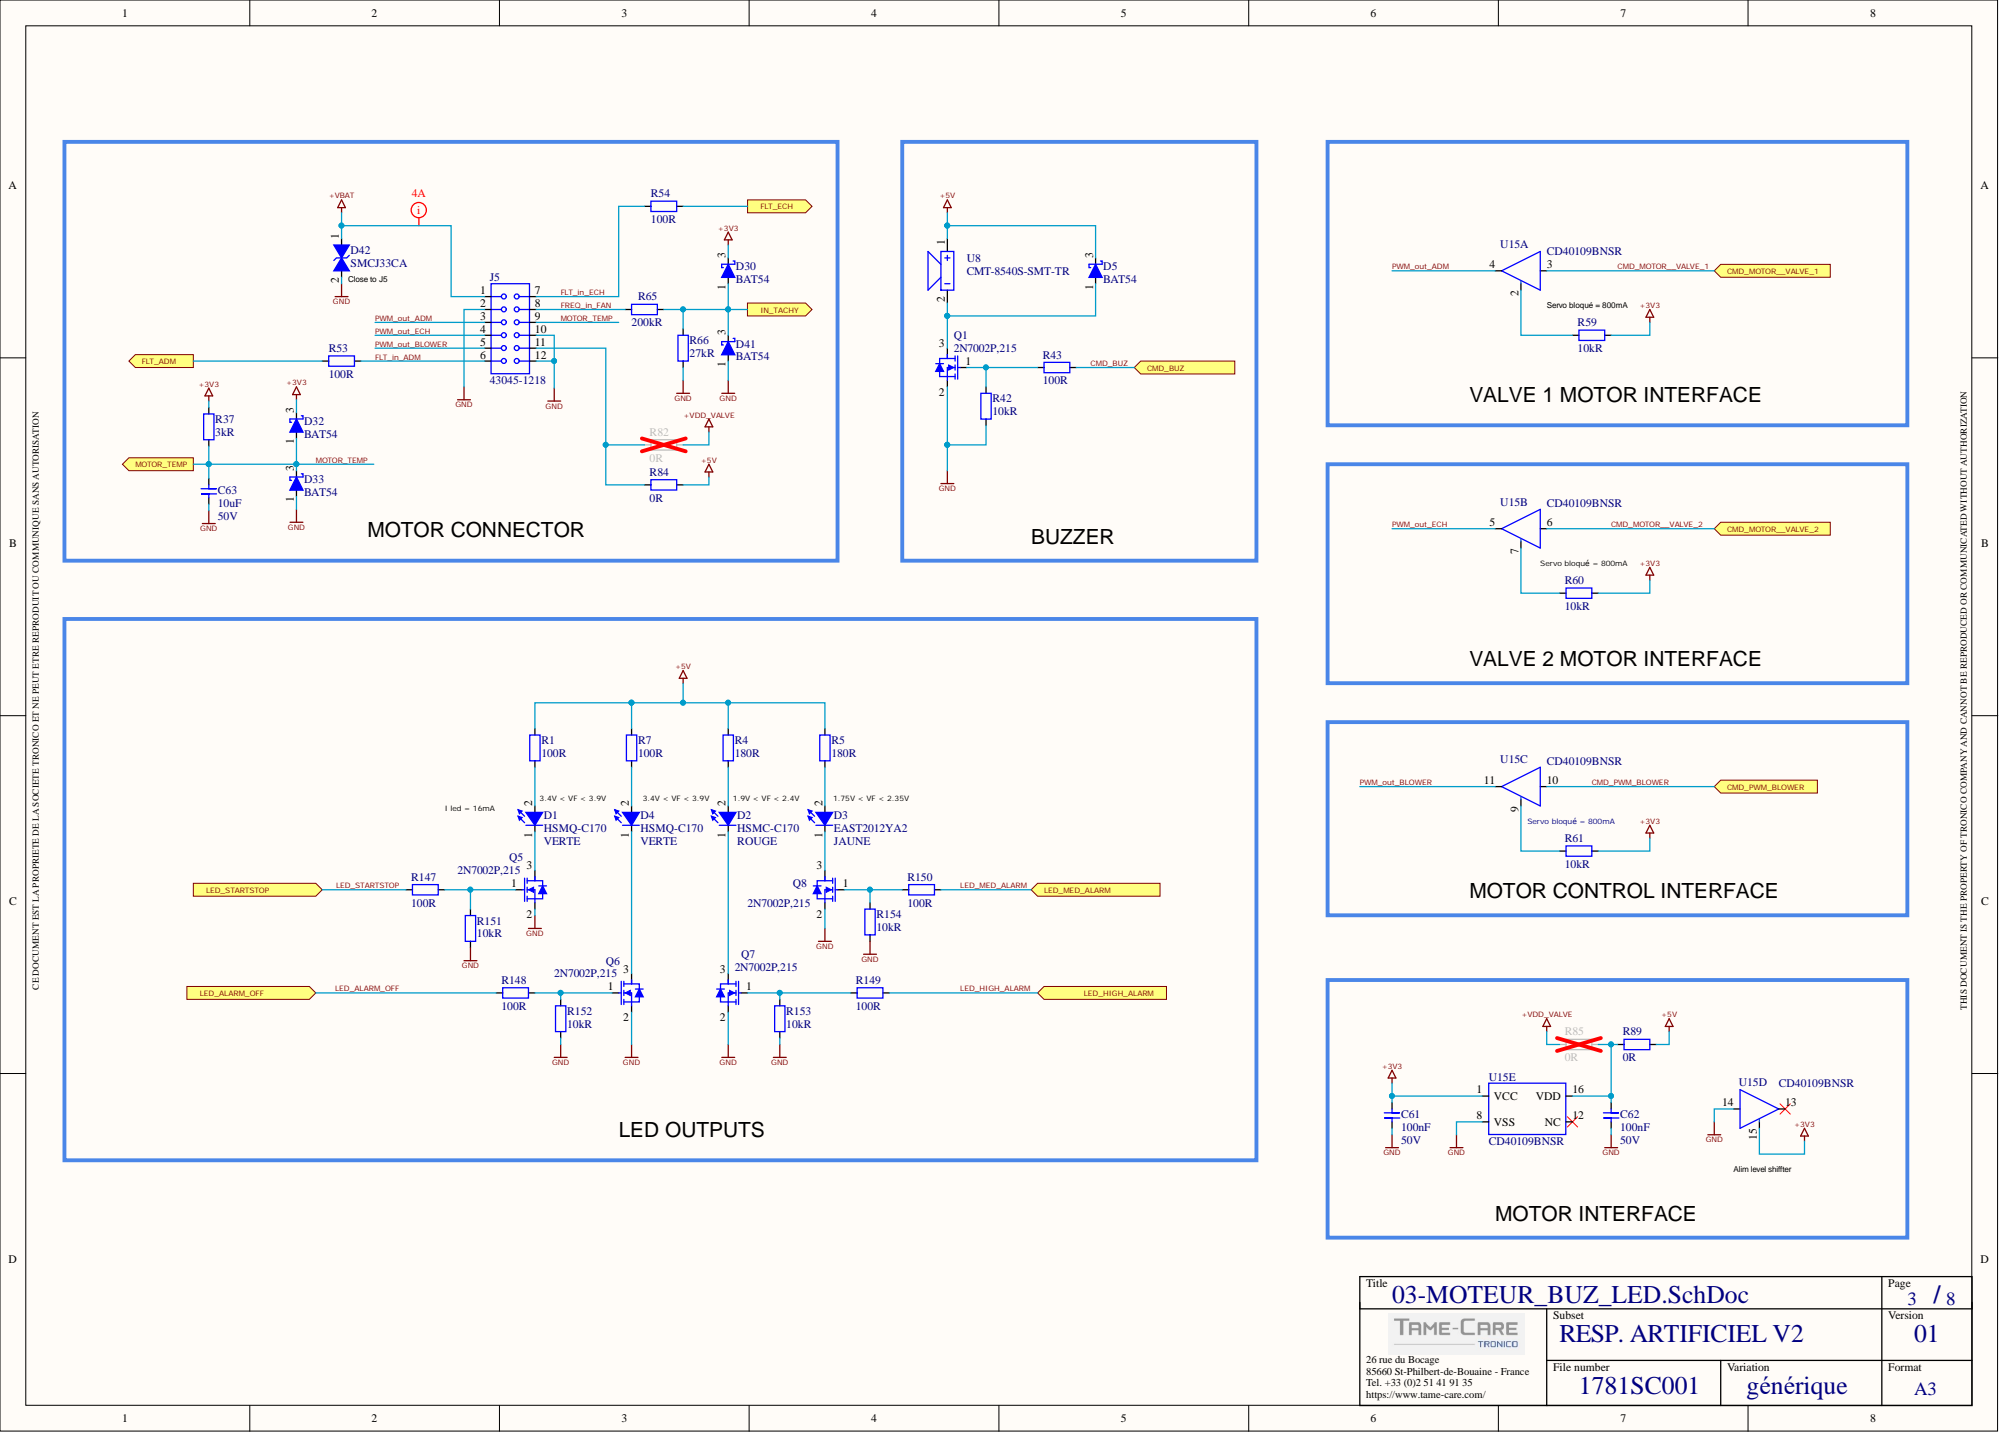
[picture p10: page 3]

THIS DOCUMENT IS THE PROPERTY OF TRONICO COMPANY AND CANNOT BE REPRODUCED OR COMMUNICATED WITHOUT AUTHORIZATION

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

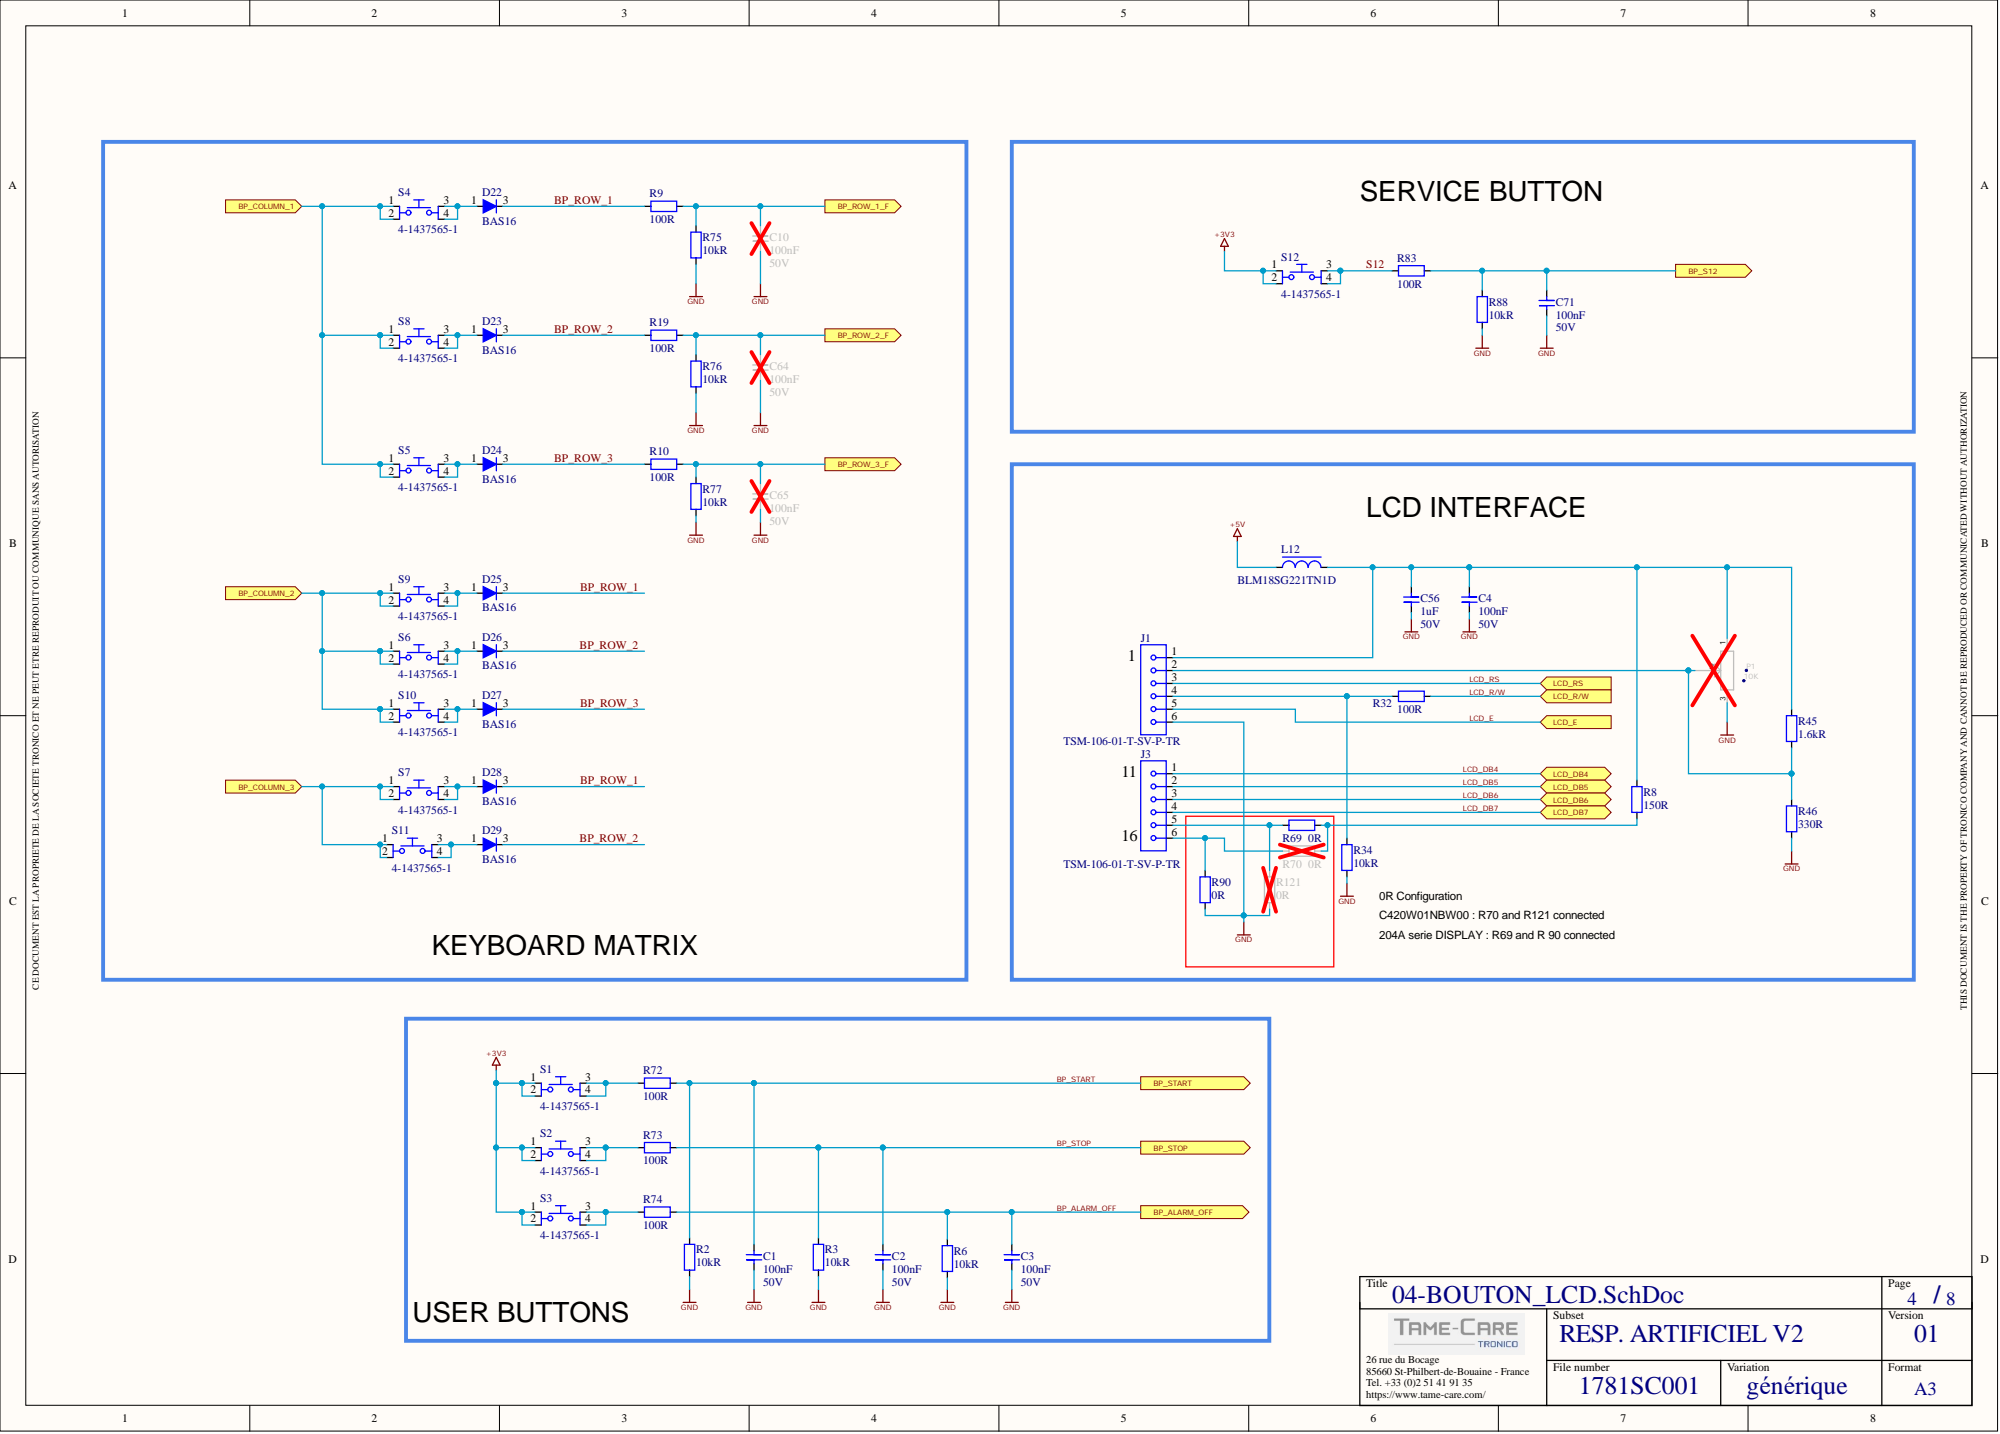
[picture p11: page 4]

THIS DOCUMENT IS THE PROPERTY OF TRONICO COMPANY AND CANNOT BE REPRODUCED OR COMMUNICATED WITHOUT AUTHORIZATION

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

C56 1uF GND GND 1 | C4 100nF 50V

1 | LCD_DB4
2 | LCD_DB5
3 | LCD_DB6

C420W01NBW00 : R70 and R121 connected
204A serie DISPLAY : R69 and R 90 connected

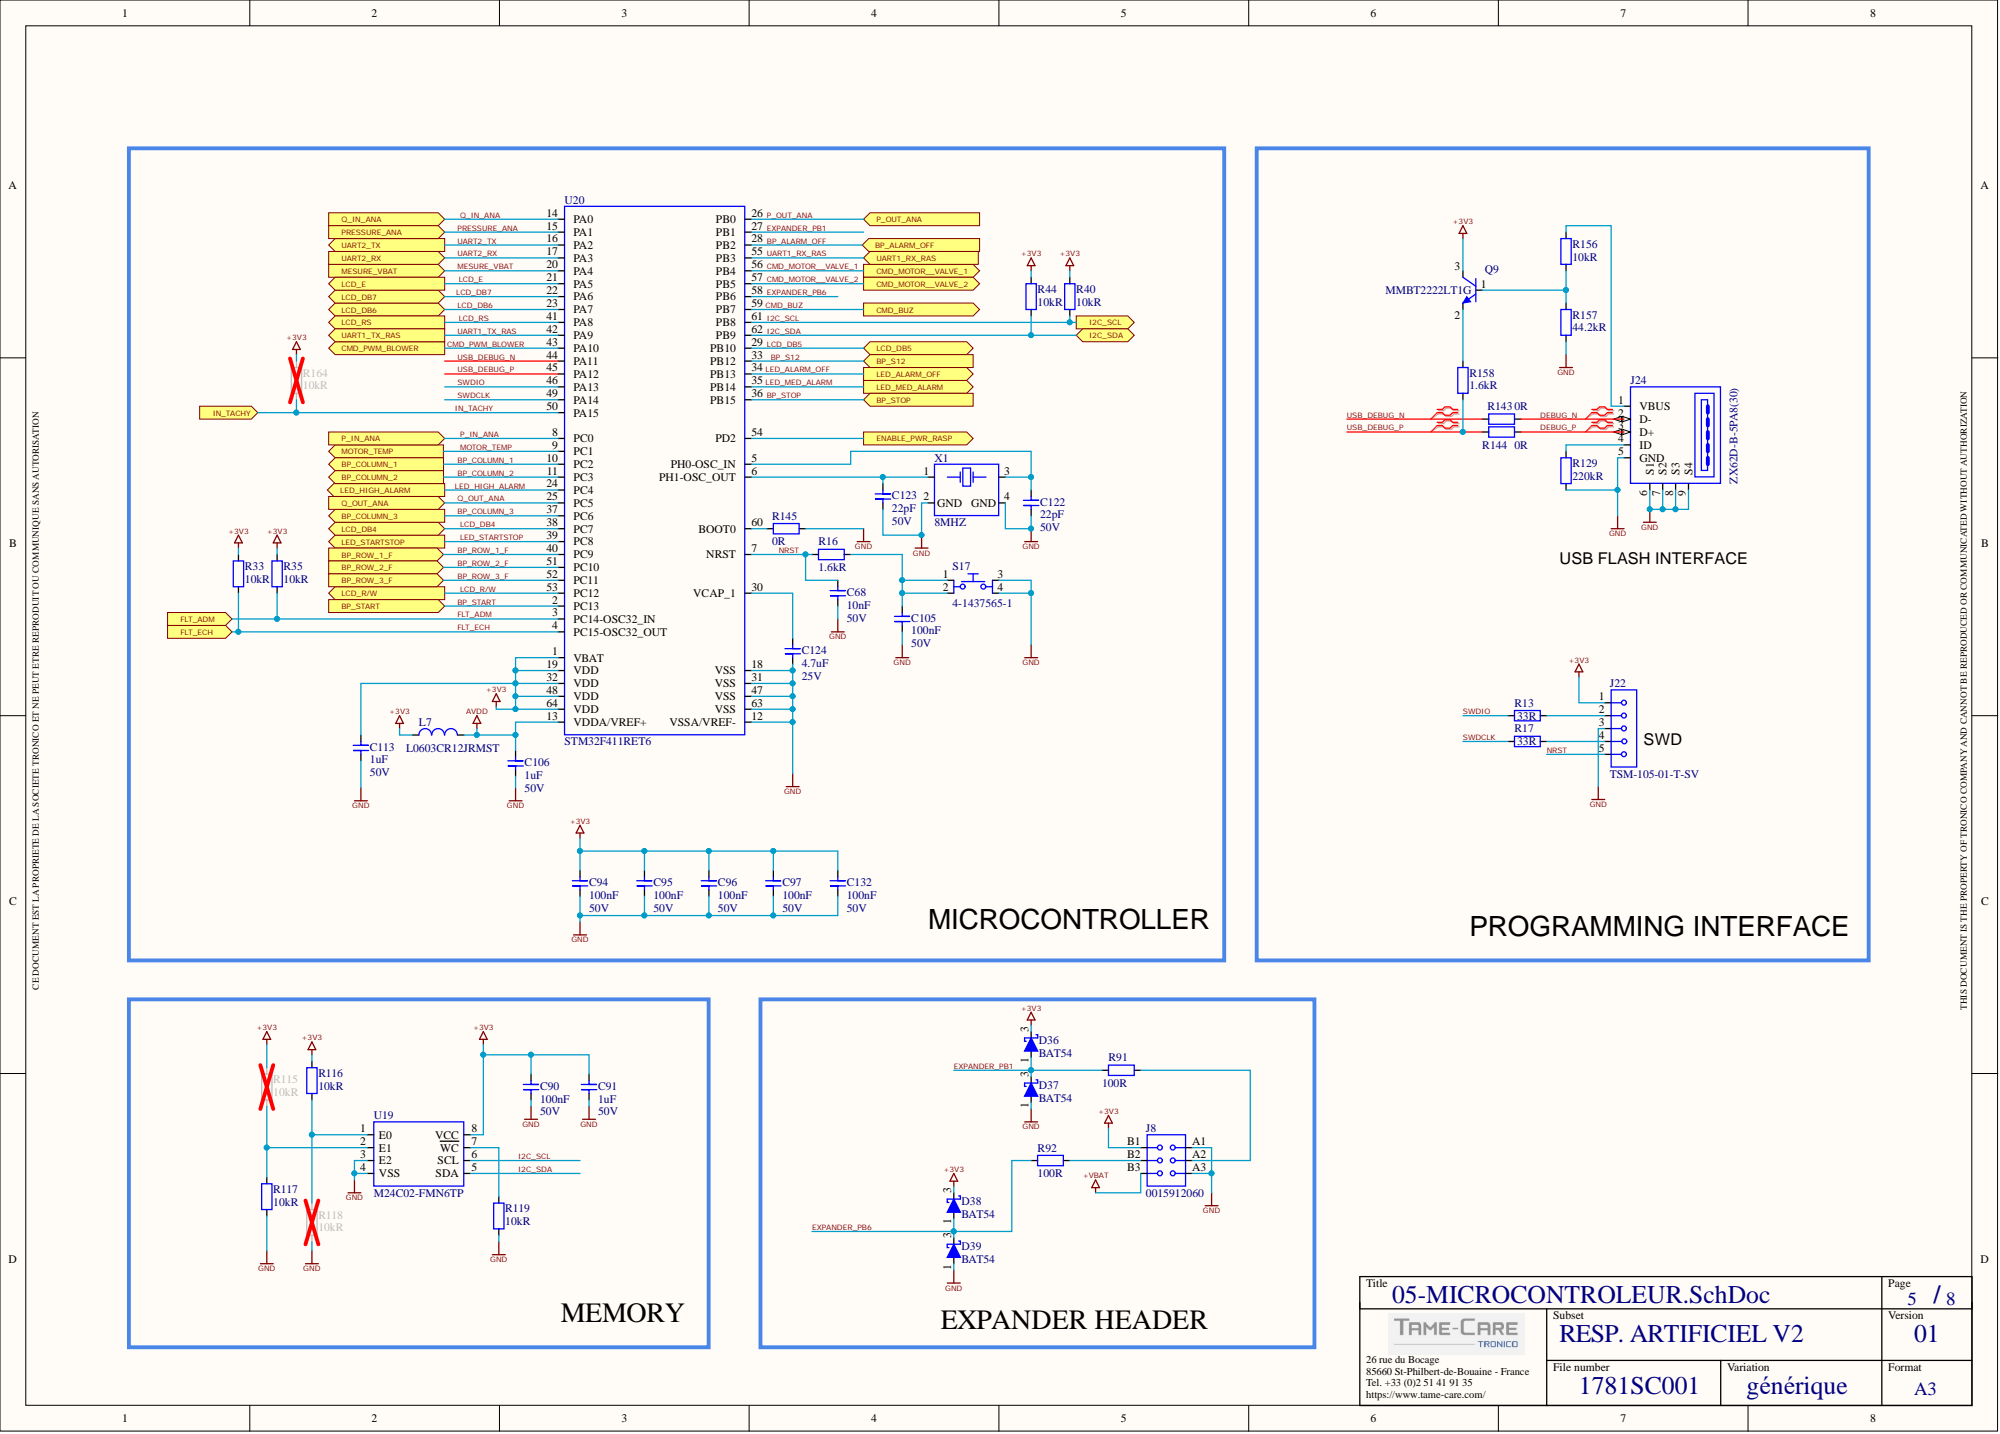
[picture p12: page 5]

THIS DOCUMENT IS THE PROPERTY OF TRONICO COMPANY AND CANNOT BE REPRODUCED OR COMMUNICATED WITHOUT AUTHORIZATION

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

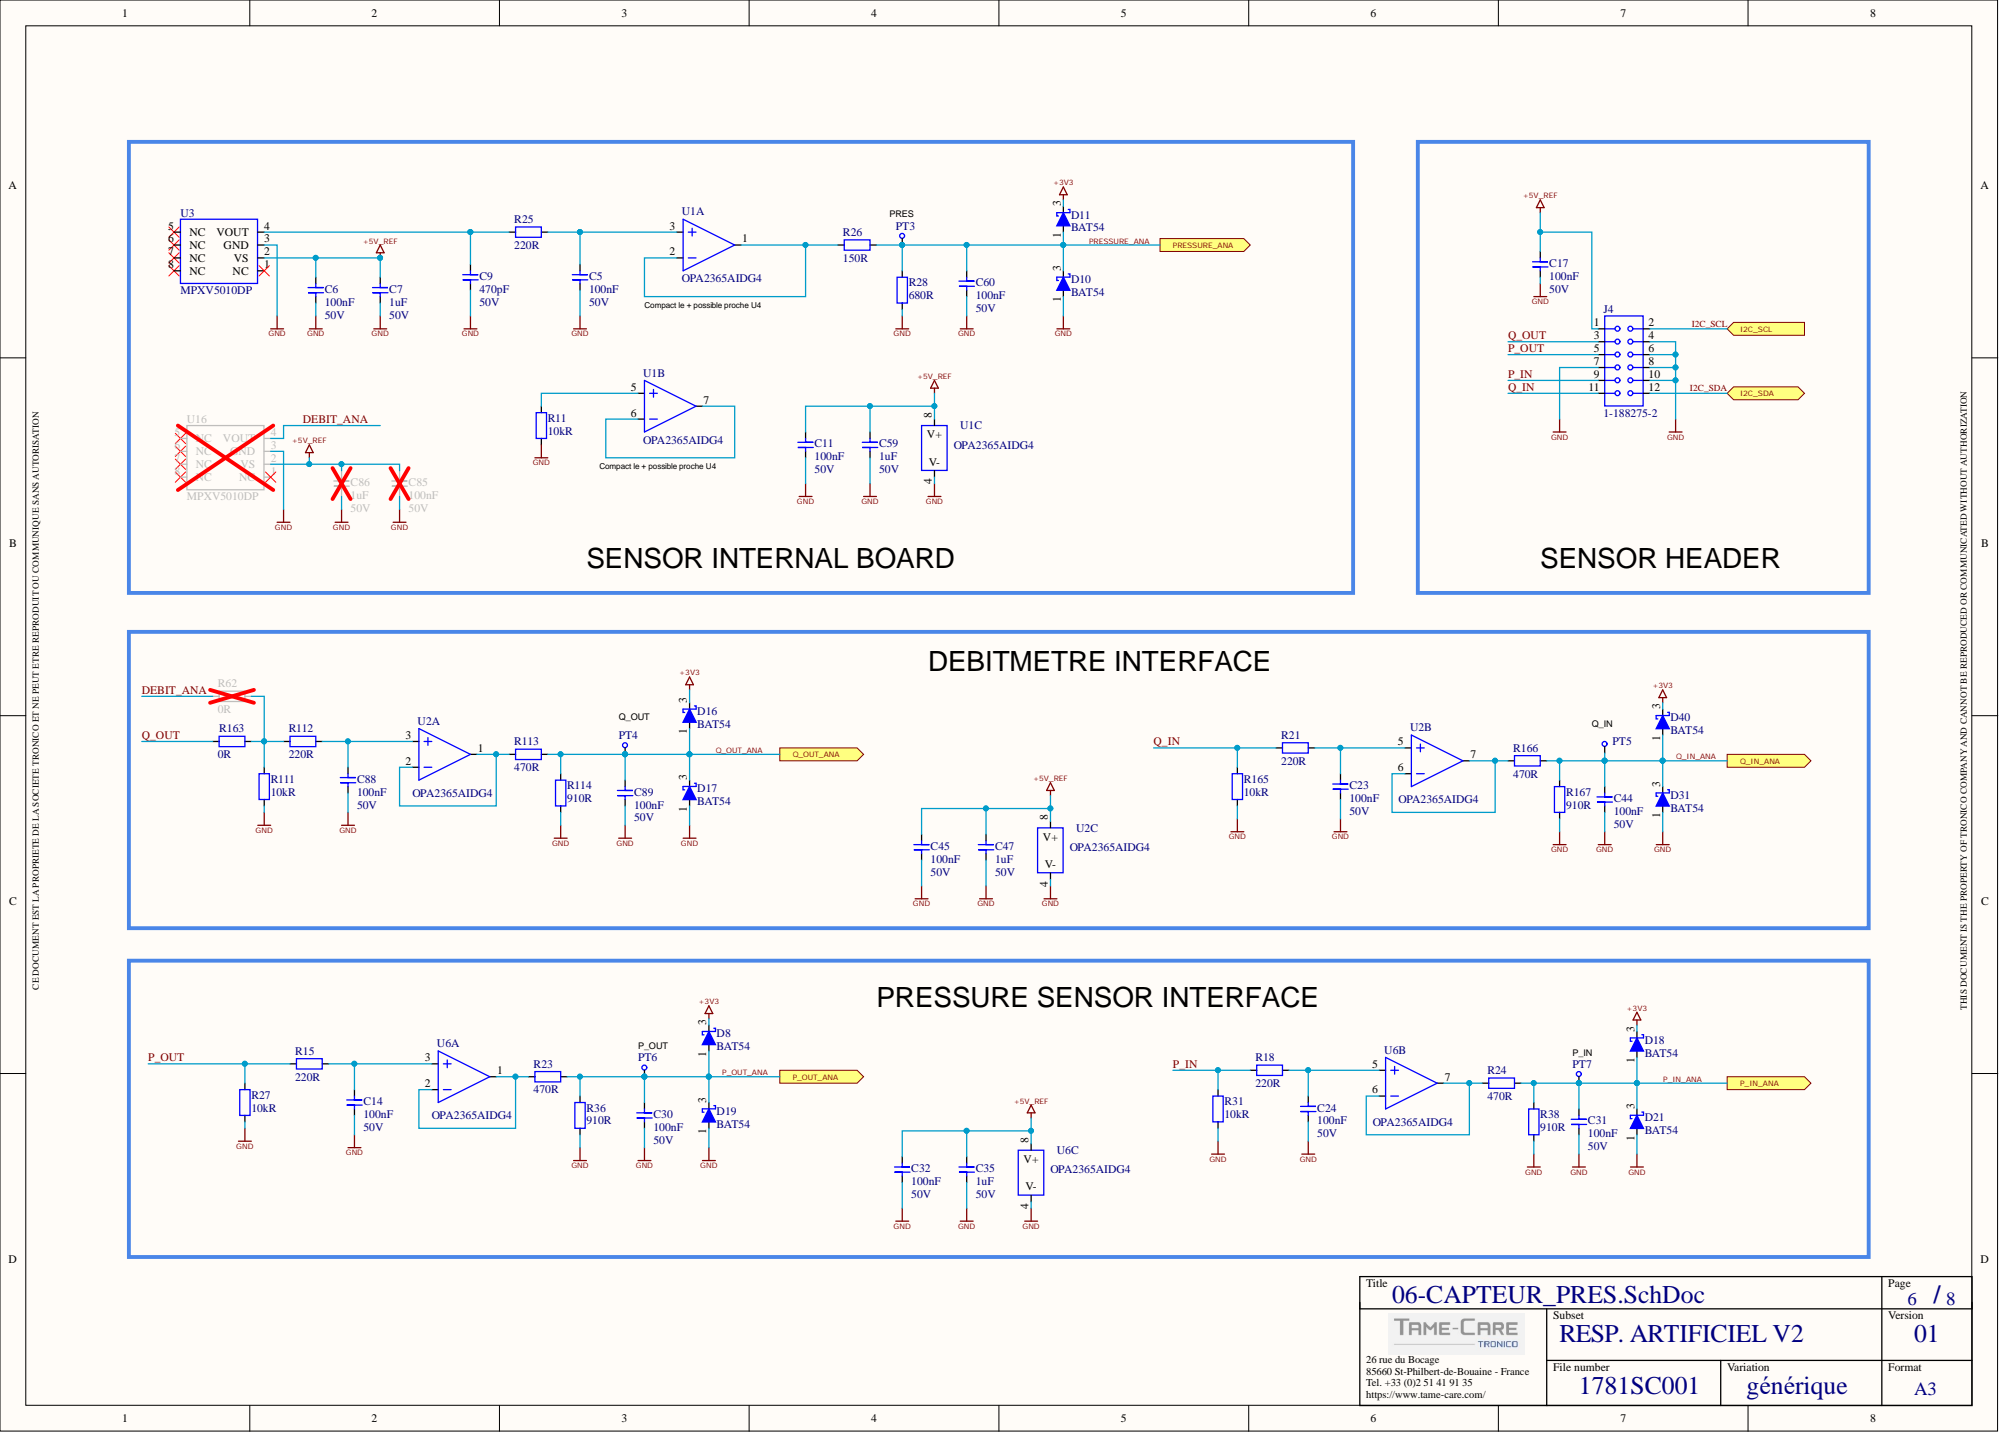
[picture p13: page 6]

Compact le + possible proche U4

THIS DOCUMENT IS THE PROPERTY OF TRONICO COMPANY AND CANNOT BE REPRODUCED OR COMMUNICATED WITHOUT AUTHORIZATION

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

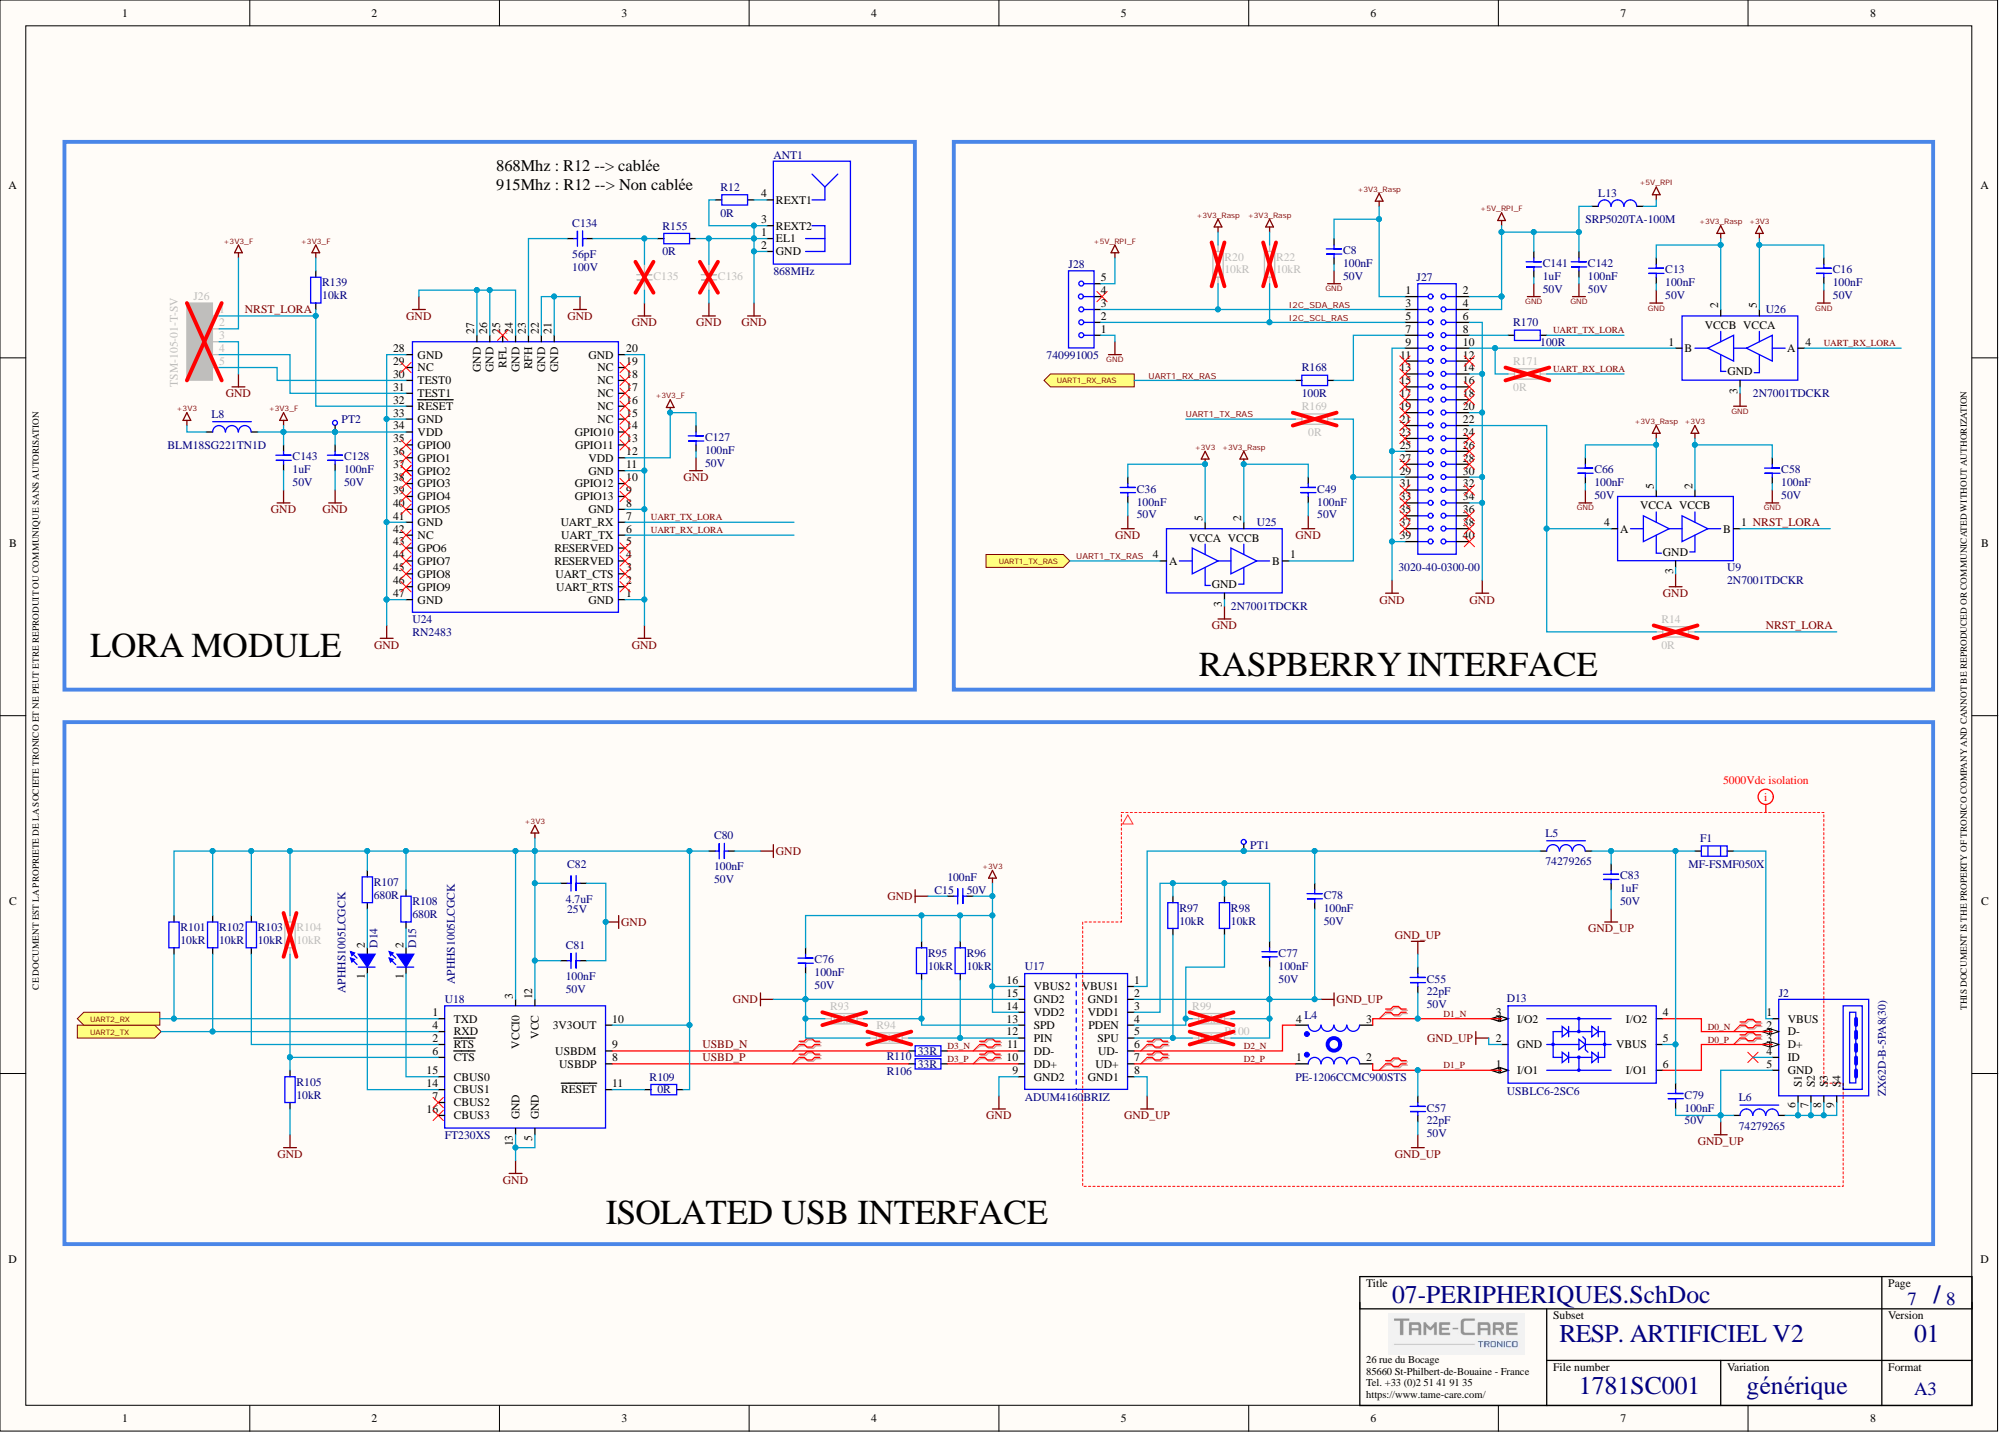
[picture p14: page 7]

THIS DOCUMENT IS THE PROPERTY OF TRONICO COMPANY AND CANNOT BE REPRODUCED OR COMMUNICATED WITHOUT AUTHORIZATION

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

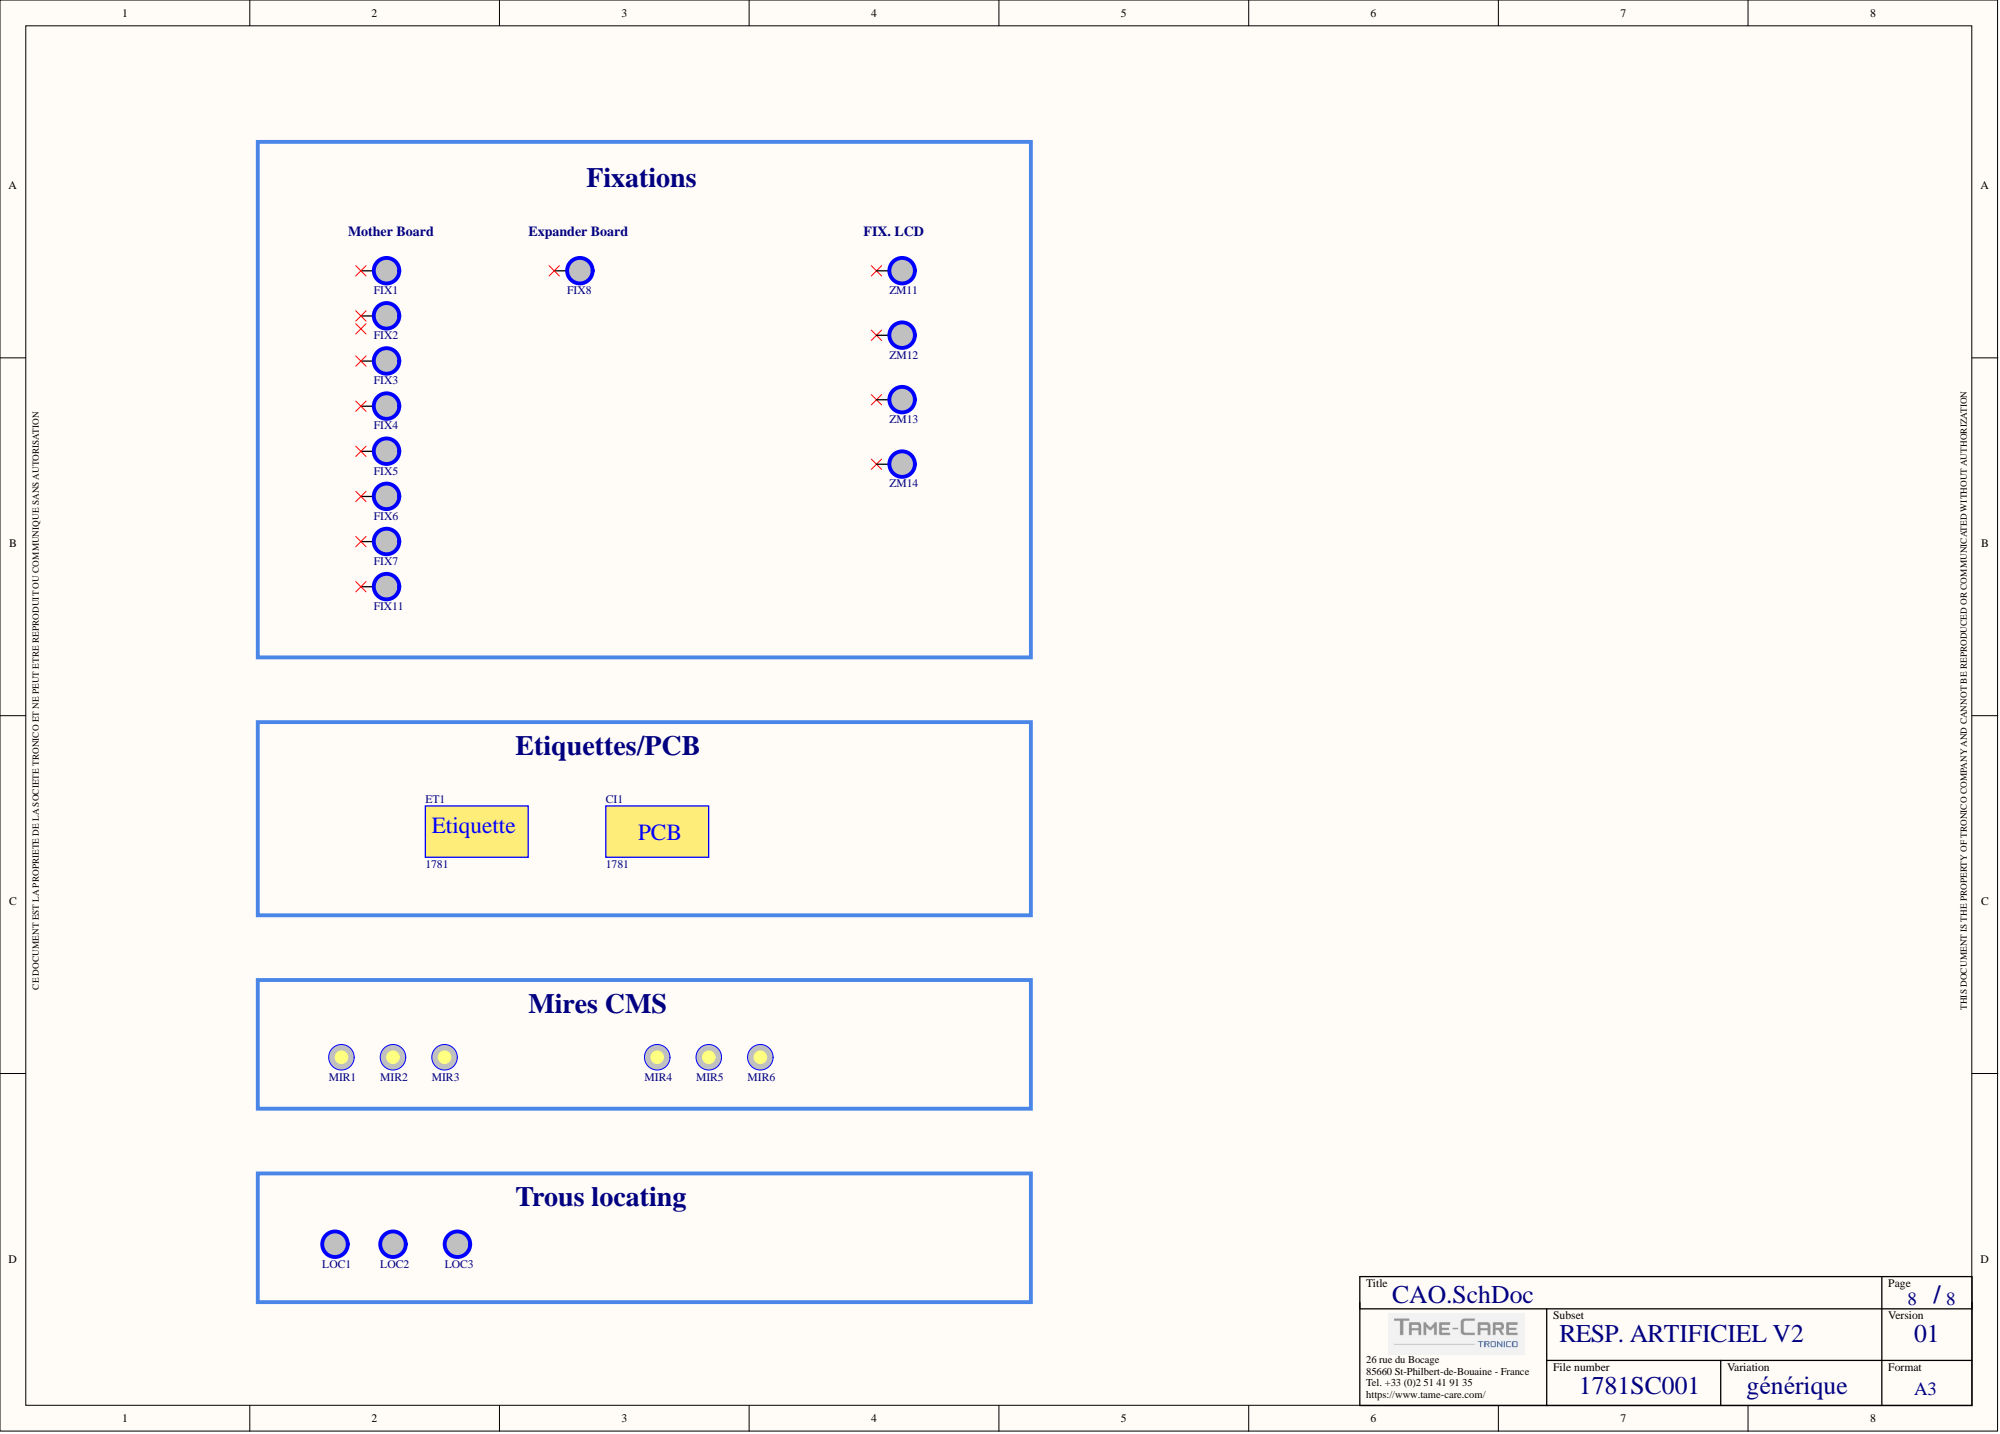
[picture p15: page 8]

THIS DOCUMENT IS THE PROPERTY OF TRONICO COMPANY AND CANNOT BE REPRODUCED OR COMMUNICATED WITHOUT AUTHORIZATION

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

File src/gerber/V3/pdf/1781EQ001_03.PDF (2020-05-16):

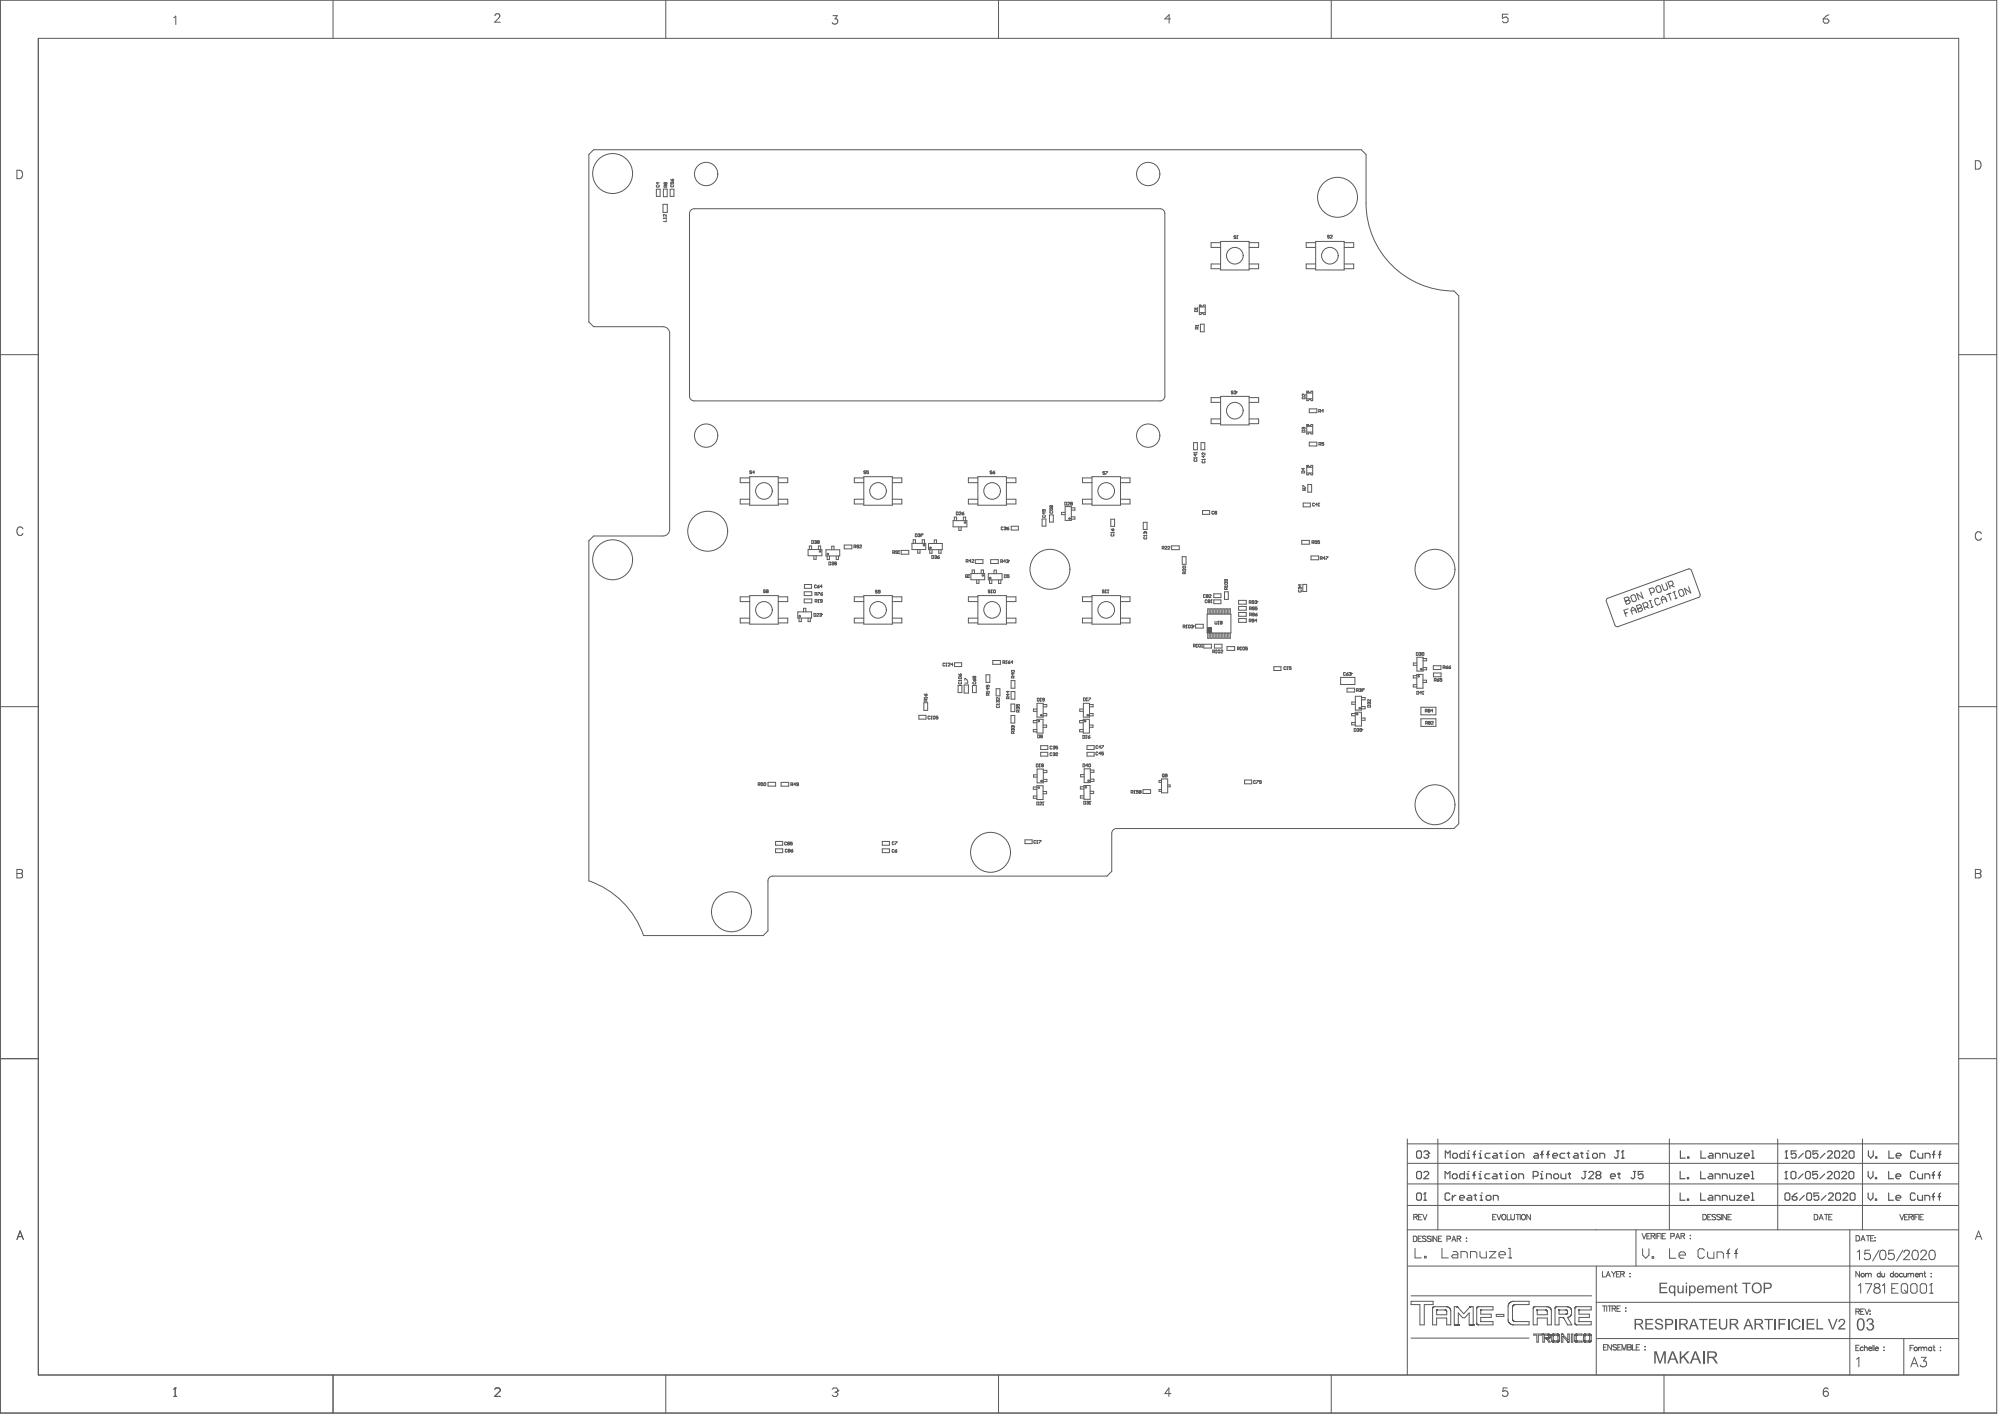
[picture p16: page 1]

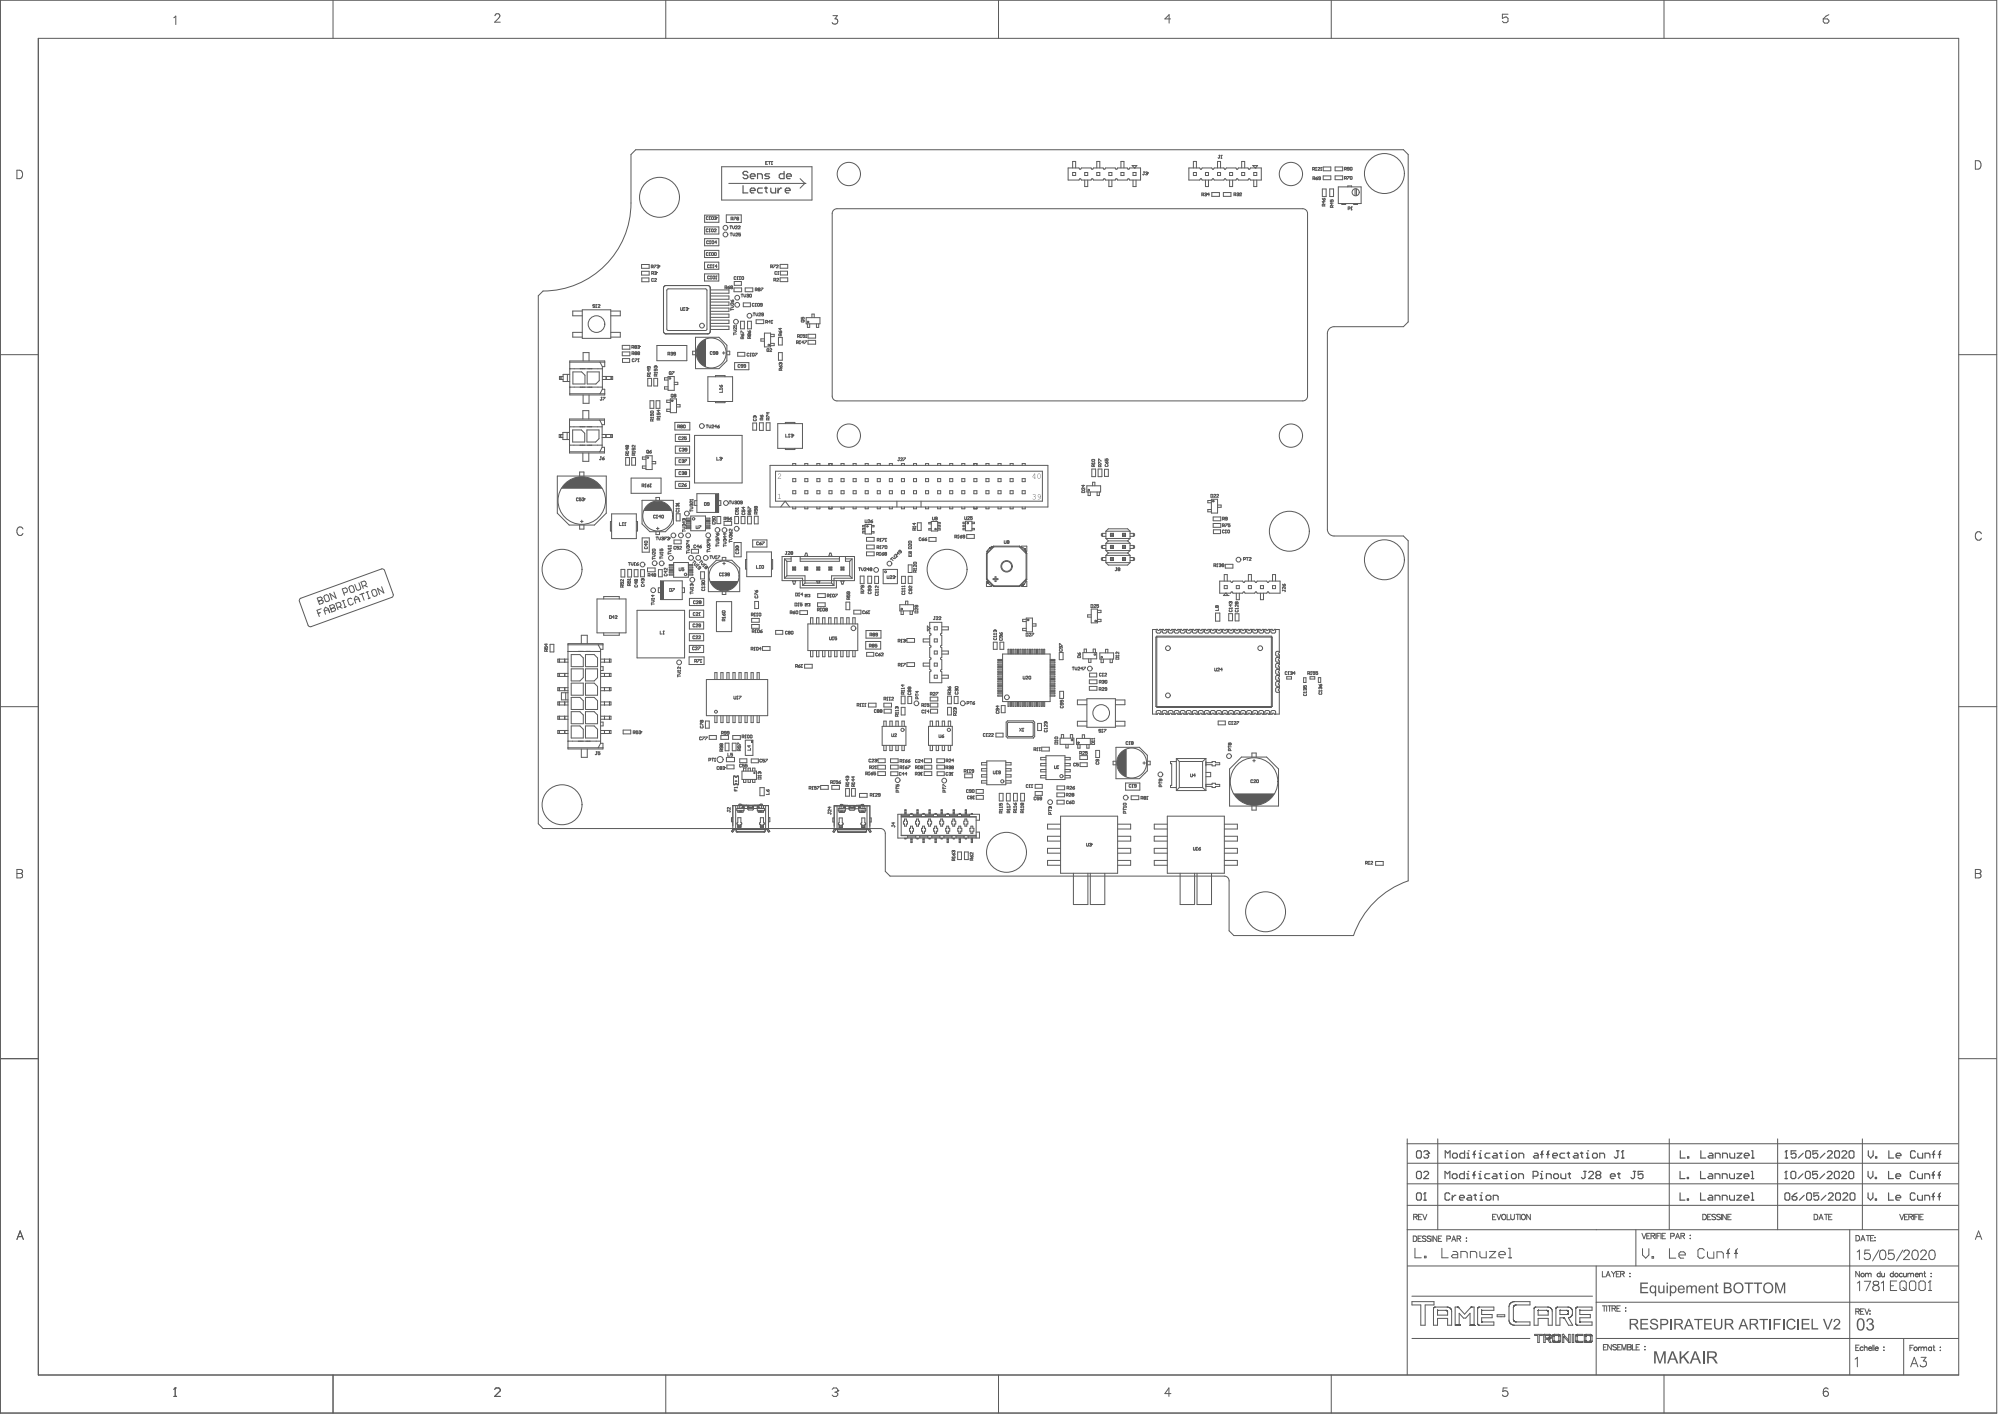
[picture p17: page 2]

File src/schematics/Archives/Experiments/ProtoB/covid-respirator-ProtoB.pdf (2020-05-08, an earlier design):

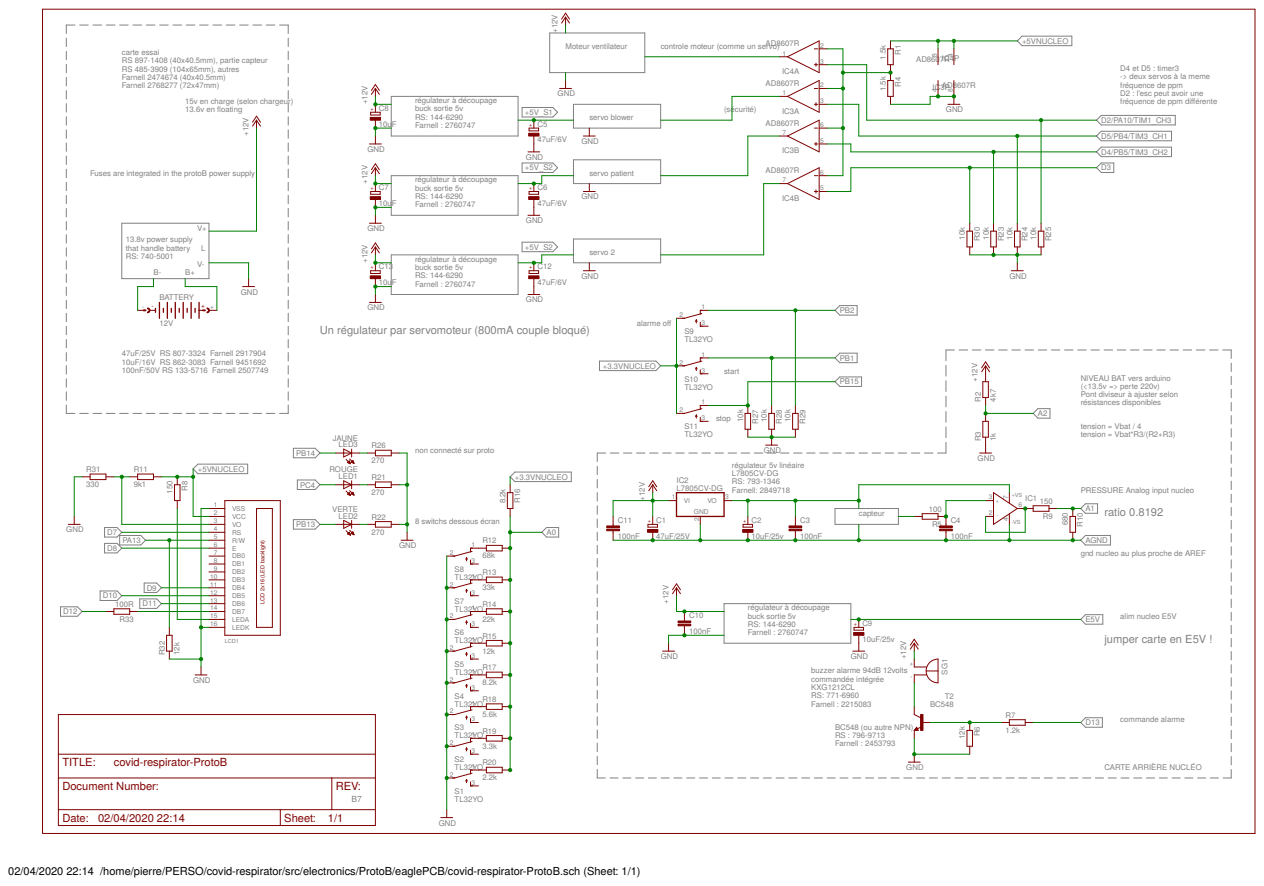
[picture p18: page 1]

carte essai
RS 897-1408 (40x40.5mm), partie capteur RS 485-3909 (104x65mm), autres Farnell 2474674 (40x40.5mm)

15v en charge (selon chargeur)
13.6v en floating

Fuses are integrated in the protoB power supply

Un régulateur par servomoteur (800mA couple bloqué)

NIVEAU BAT vers arduino
(<13.5v => perte 220v)
Pont diviseur à ajuster selon
résistances disponibles

non connecté sur proto

AGND
gnd nucleo au plus proche de AREF

Document Number: | REV: B7

Date: 02/04/2020 22:14 | Sheet: 1/1

02/04/2020 22:14 /home/pierre/PERSO/covid-respirator/src/electronics/ProtoB/eaglePCB/covid-respirator-ProtoB.sch (Sheet: 1/1)

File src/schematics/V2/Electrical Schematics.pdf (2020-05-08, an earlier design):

A | A

# 01-ALIM_1/2

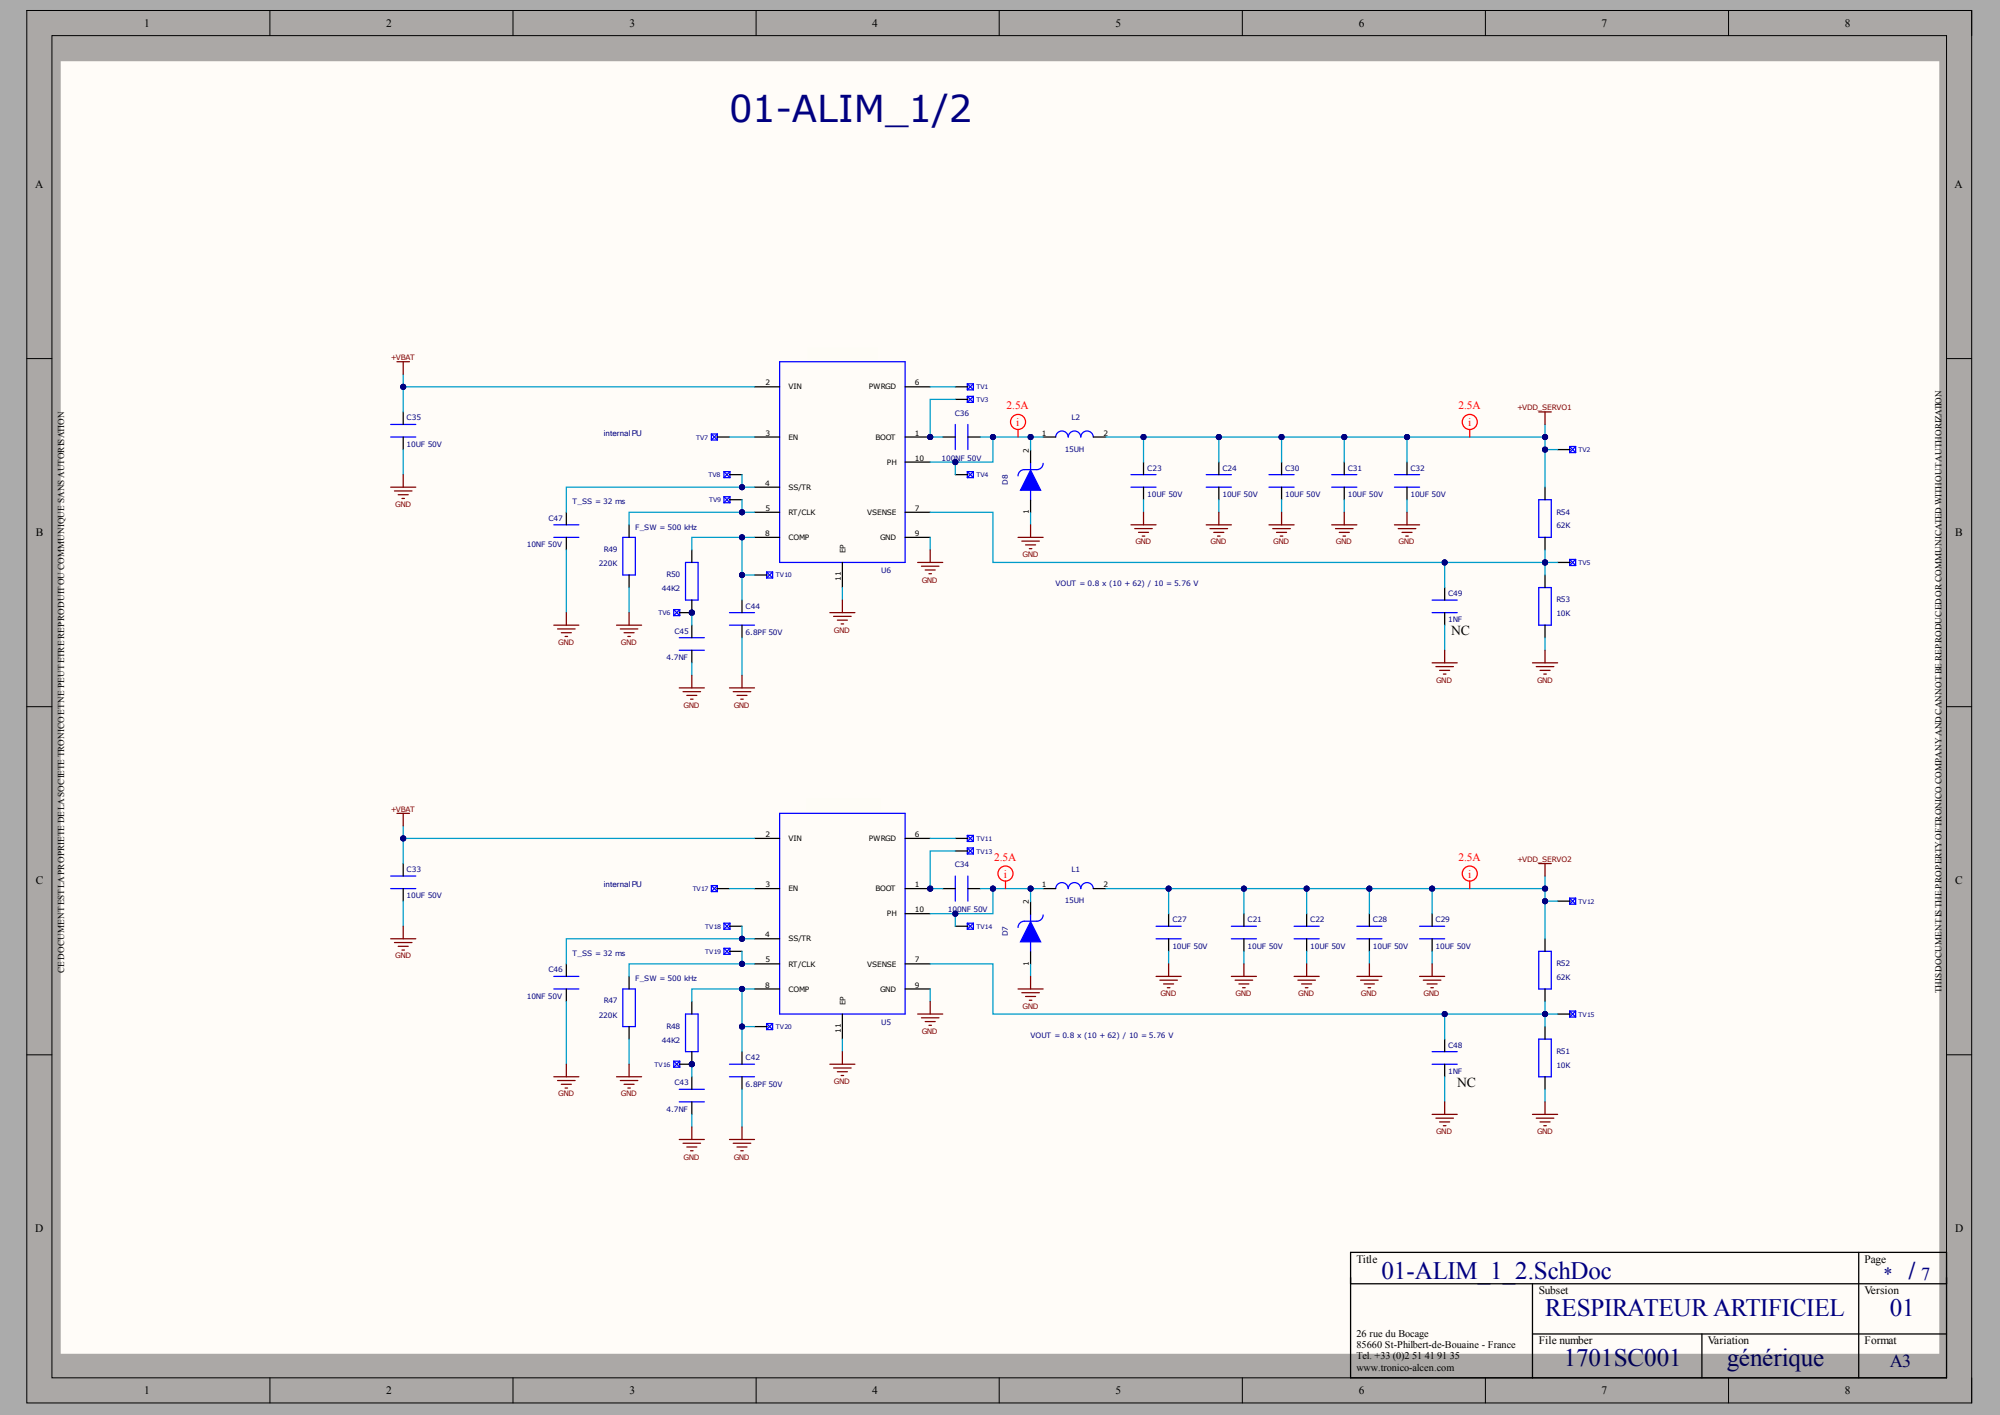
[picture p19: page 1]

THIS DOCUMENTISTHE PROPERTY OFTRONICO COMPANY AND CANNOTBE REPRODUCED OR COMMUNICATED WITHOUTAUTHORIZATION

CE DOCUMENTESTLA PROPRIETE DELA SOCIETE TRONICO ETNE PEUTETRE REPRODUITOU COMMUNIQUE SANSAUTORISATION

Title LIM_1_2.SchDoc | Page 01-A * / 7

26 rue du Bocage 85660 St-Philbert-de-Bouaine - France Tel. +33 (0)2 51 41 91 35 | Subset RES PIRATEUR A RTIFICIEL | Version 01

File number 1701 SC001 | Variation générique | Format

www.tronico-alcen.com | | | A3

A | A

# 02-ALIM_2/2


Au plus proche du connecteur du capteur pression

THIS DOCUMENTISTHE PROPERTY OFTRONICO COMPANY AND CANNOTBE REPRODUCED OR COMMUNICATED WITHOUTAUTHORIZATION

CE DOCUMENTESTLA PROPRIETE DELA SOCIETE TRONICO ETNE PEUTETRE REPRODUITOU COMMUNIQUE SANSAUTORISATION

Title LIM_2_2.SchDoc | Page 02-A * / 7

Subset | Version

A | A

# 03-MOTEUR_BUZ_LED


THIS DOCUMENTISTHE PROPERTY OFTRONICO COMPANY AND CANNOTBE REPRODUCED OR COMMUNICATED WITHOUTAUTHORIZATION

CE DOCUMENTESTLA PROPRIETE DELA SOCIETE TRONICO ETNE PEUTETRE REPRODUITOU COMMUNIQUE SANSAUTORISATION

CTN TEMPERATURE MOTEUR
DEPORTEE OU KLIXON (ON/OFF)

Title Z_LED.SchDoc | Page 03-MOTEUR_BU * / 7

Subset | Version

A | A

# 04-LCD_BOUTO


THIS DOCUMENTISTHE PROPERTY OFTRONICO COMPANY AND CANNOTBE REPRODUCED OR COMMUNICATED WITHOUTAUTHORIZATION

CE DOCUMENTESTLA PROPRIETE DELA SOCIETE TRONICO ETNE PEUTETRE REPRODUITOU COMMUNIQUE SANSAUTORISATION

Title TON_LCD.SchDoc | Page 04-BOU * / 7

Subset | Version

A | A

# 05-CNX_NUCLEO


THIS DOCUMENTISTHE PROPERTY OFTRONICO COMPANY AND CANNOTBE REPRODUCED OR COMMUNICATED WITHOUTAUTHORIZATION

CE DOCUMENTESTLA PROPRIETE DELA SOCIETE TRONICO ETNE PEUTETRE REPRODUITOU COMMUNIQUE SANSAUTORISATION

Title | Page 05-CNX_NUCLEO.SchDoc * / 7

Subset | Version

A | A

# 06-CAPTEUR_PRESSI


Compact le +possible proche U4

THIS DOCUMENTISTHE PROPERTY OFTRONICO COMPANY AND CANNOTBE REPRODUCED OR COMMUNICATED WITHOUTAUTHORIZATION

CE DOCUMENTESTLA PROPRIETE DELA SOCIETE TRONICO ETNE PEUTETRE REPRODUITOU COMMUNIQUE SANSAUTORISATION

Title P TEUR_PRES.SchDoc | Page 06-CA * / 7

Subset | Version

A | A

## Fixations

FIX1; MT32VIA; FIX2; FIX3; FIX4; FIX5; FIX6; GND; Etiquettes/PCB; Mires CMS; Trous locating; PCB; Etiquette; MIR1; MIR2; MIR3; MIR4; MIR5; MIR6; LOC1; LOC2; LOC3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

THIS DOCUMENTISTHE PROPERTY OFTRONICO COMPANY AND CANNOTBE REPRODUCED OR COMMUNICATED WITHOUTAUTHORIZATION

CE DOCUMENTESTLA PROPRIETE DELA SOCIETE TRONICO ETNE PEUTETRE REPRODUITOU COMMUNIQUE SANSAUTORISATION

Title | Page CAO.SchDoc * / 7

Subset | Version

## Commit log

2020-05-08 Import motherboard files from core repository (split)
    [covid-respirator-ProtoB.brd, covid-respirator-ProtoB.sch, respi_V0.fzz]
2020-05-16 Gerbers mother board
    [1781GER001_03.DRL, 1781GER001_03.GBL, 1781GER001_03.GBO, 1781GER001_03.GBP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]
2020-05-16 Re-organize V3 files structure
    [1781GER001_03.DRL, 1781GER001_03.GBL, 1781GER001_03.GBO, 1781GER001_03.GBP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]
2020-12-30 Add PbAc battery Kt data
    [pbac-kt_v-cmv.csv]
